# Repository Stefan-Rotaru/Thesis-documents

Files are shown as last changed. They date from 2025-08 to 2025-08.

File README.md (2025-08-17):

#Thesis code
Roll stabilization lab
==================================

Prerequisites
-------------
• Python 3.12+  
• Arduino IDE  
• Servo.h Arduino Library (https://www.arduino.cc/reference/en/libraries/servo/)

Usage
-----
1. Upload the controller to the Arduino:
   - Plug-in the Arduino board  
   - Open the "PID_Arduino" file,  then the "PID_Arduino.ino" script  
   - Select your board and port  
   - Click Upload

2. Record data to a text file:  
   - python script.py

3. Plot the data :
  - python plots.py --trim= a test_b.txt
  - Replace a by the trim needed
  - Replace b by the test to plot

Configuration
-------------
 - In "PID_Arduino.ino" (line 175) tweak "Kp", "Ki", "Kd" to tune your controller.
 - On line 160 of "PID_Arduino.ino" you can change the “setpoint” for your target roll angle.
 - In "script.py" make sure the serial "port = 'COM3'" matches your board.

Encoder error
-------------
Spikes might occur due to encoder's measurement error

#Solidworks Assembly 3D
=======================
Contains the solidworks files. Assem1 is the whole assembly of the device

#Thesis video
=============
Contains the videos of the experimental tests. They are also available in the issues tab.

#Technical drawings
===================
Contrains the technical drawings of the aluminium machined version of the device

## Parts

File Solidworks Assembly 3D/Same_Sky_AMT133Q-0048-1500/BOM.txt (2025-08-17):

3DX_Same_Sky_Supplier: Same Sky
3DX_Same_Sky_Description: AMT13 Axial, Quadrature Line Driver, 48 PPR, 15 mm Bore
3DX_Same_Sky_Part Number: AMT133Q-0048-1500

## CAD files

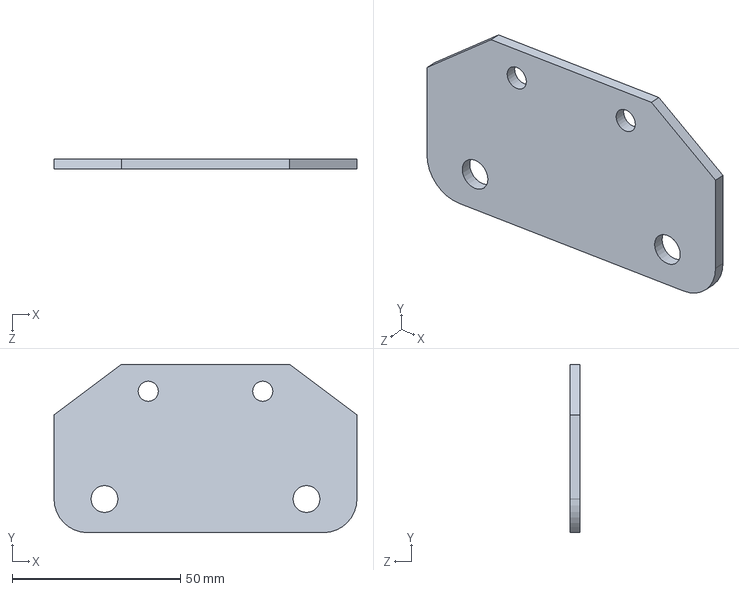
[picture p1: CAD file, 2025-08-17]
Solidworks Assembly 3D/Attachement a la base.SLDPRT
90.0 x 50.0 x 3.00 mm

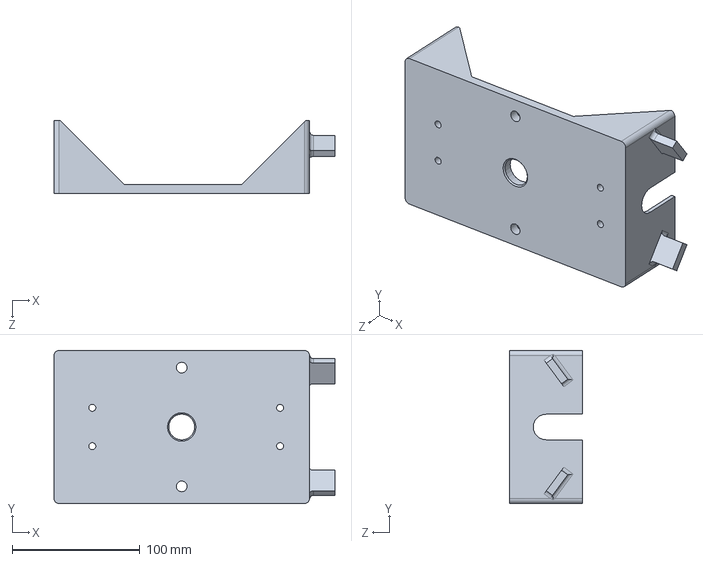
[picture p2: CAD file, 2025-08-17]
Solidworks Assembly 3D/chassis.SLDPRT
220.0 x 120.0 x 57.0 mm

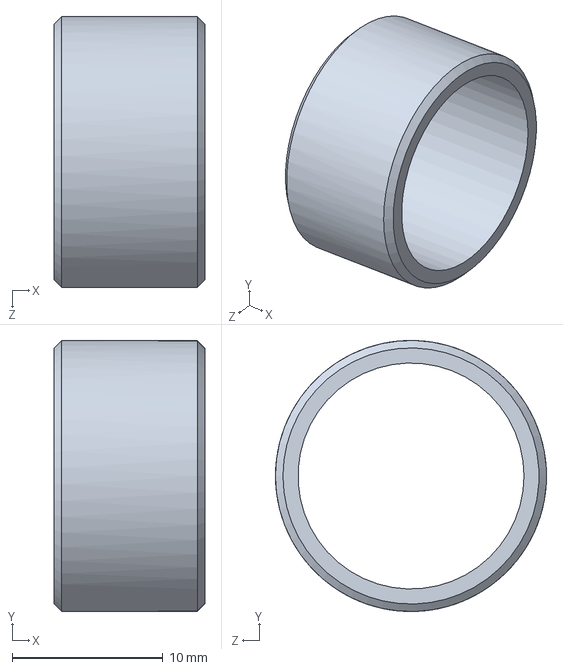
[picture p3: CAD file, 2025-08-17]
Solidworks Assembly 3D/Part1.SLDPRT
10.0 x 18.0 x 18.0 mm

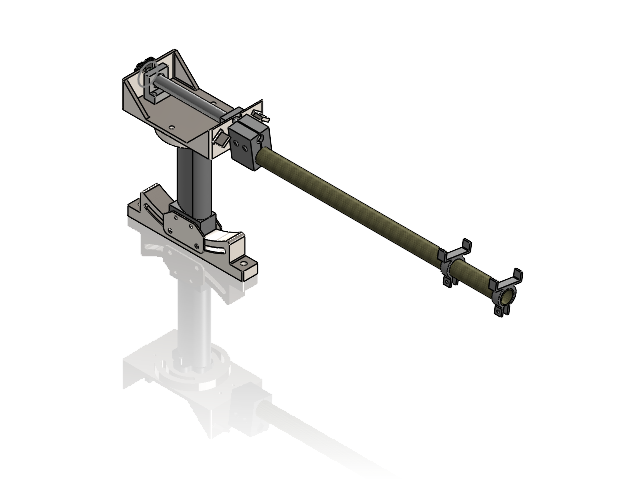
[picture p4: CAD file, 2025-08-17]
Solidworks Assembly 3D/Assem1.SLDASM
Base arc de cercle
Support
Attachement a la base x 2
Support dervie
Spacer
RCB6-30 x 2
PSFAJEU20-164-F40-P15-T60
chassis
BGLKS6902ZZ-30_b x 2
bearing_6902 x 2
RRING28 x 2
shaft_holders x 2
shaft_carbon
Same_Sky_SPACER_AMT13
Same_Sky_PIN_AMT13 x 6
Same_Sky_PIN_2_5MM-4_7MM x 2
Same_Sky_RECEIVER_PCB_AMT13
Same_Sky_ROTOR_AMT13
Same_Sky_SET_SCREW_2_5D-3L-0_45P
Same_Sky_HUB_15MM
Same_Sky_TRANSMITER_PCB_AMT13
Same_Sky_BM18B-ZPDSS-TF
Same_Sky_INJECTION_MOLDING_CHASSIS
Same_Sky_INJECTION_MOLDING_COVER
Berceau x 2

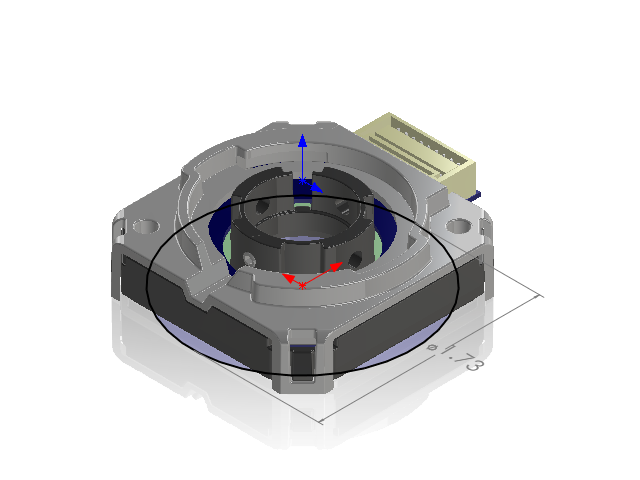
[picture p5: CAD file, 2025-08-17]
Solidworks Assembly 3D/Same_Sky_AMT133Q-0048-1500/Same_Sky_CUI_DEVICES_AMT133S-0048-1500.SLDASM
Same_Sky_SPACER_AMT13
Same_Sky_PIN_AMT13 x 6
Same_Sky_PIN_2_5MM-4_7MM x 2
Same_Sky_RECEIVER_PCB_AMT13
Same_Sky_ROTOR_AMT13
Same_Sky_SET_SCREW_2_5D-3L-0_45P
Same_Sky_HUB_15MM
Same_Sky_TRANSMITER_PCB_AMT13
Same_Sky_BM18B-ZPDSS-TF
Same_Sky_INJECTION_MOLDING_CHASSIS
Same_Sky_INJECTION_MOLDING_COVER

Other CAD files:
Solidworks Assembly 3D/Same_Sky_AMT133Q-0048-1500/Same_Sky_TRANSMITER_PCB_AMT13(Axial).SLDASM
Solidworks Assembly 3D/Bumper/ULBYS20-30-M8.sldasm
Solidworks Assembly 3D/SOLIDWORKS/BGLKS6902ZZ-30.sldasm
Solidworks Assembly 3D/Same_Sky_AMT133Q-0048-1500/Same_Sky_ROTOR_AMT13(1500).SLDASM
Solidworks Assembly 3D/Same_Sky_AMT133Q-0048-1500/Same_Sky_RECEIVER_PCB_ASM.SLDASM
Solidworks Assembly 3D/Same_Sky_AMT133Q-0048-1500/Same_Sky_SPACER_AMT13_ASM.SLDASM
Solidworks Assembly 3D/Same_Sky_AMT133Q-0048-1500/Same_Sky_PCB_AMT13(Axial, 1500).SLDASM
Solidworks Assembly 3D/Bumper/ULBYS20-30-M8_b.sldprt
Solidworks Assembly 3D/Same_Sky_AMT133Q-0048-1500/Same_Sky_INJECTION_MOLDING_CHASSIS.SLDPRT
Solidworks Assembly 3D/SOLIDWORKS/RRING28.sldprt
Solidworks Assembly 3D/Bumper/SCB8-12_1.sldprt
Solidworks Assembly 3D/SOLIDWORKS/BGLKS6902ZZ-30_b.sldprt
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

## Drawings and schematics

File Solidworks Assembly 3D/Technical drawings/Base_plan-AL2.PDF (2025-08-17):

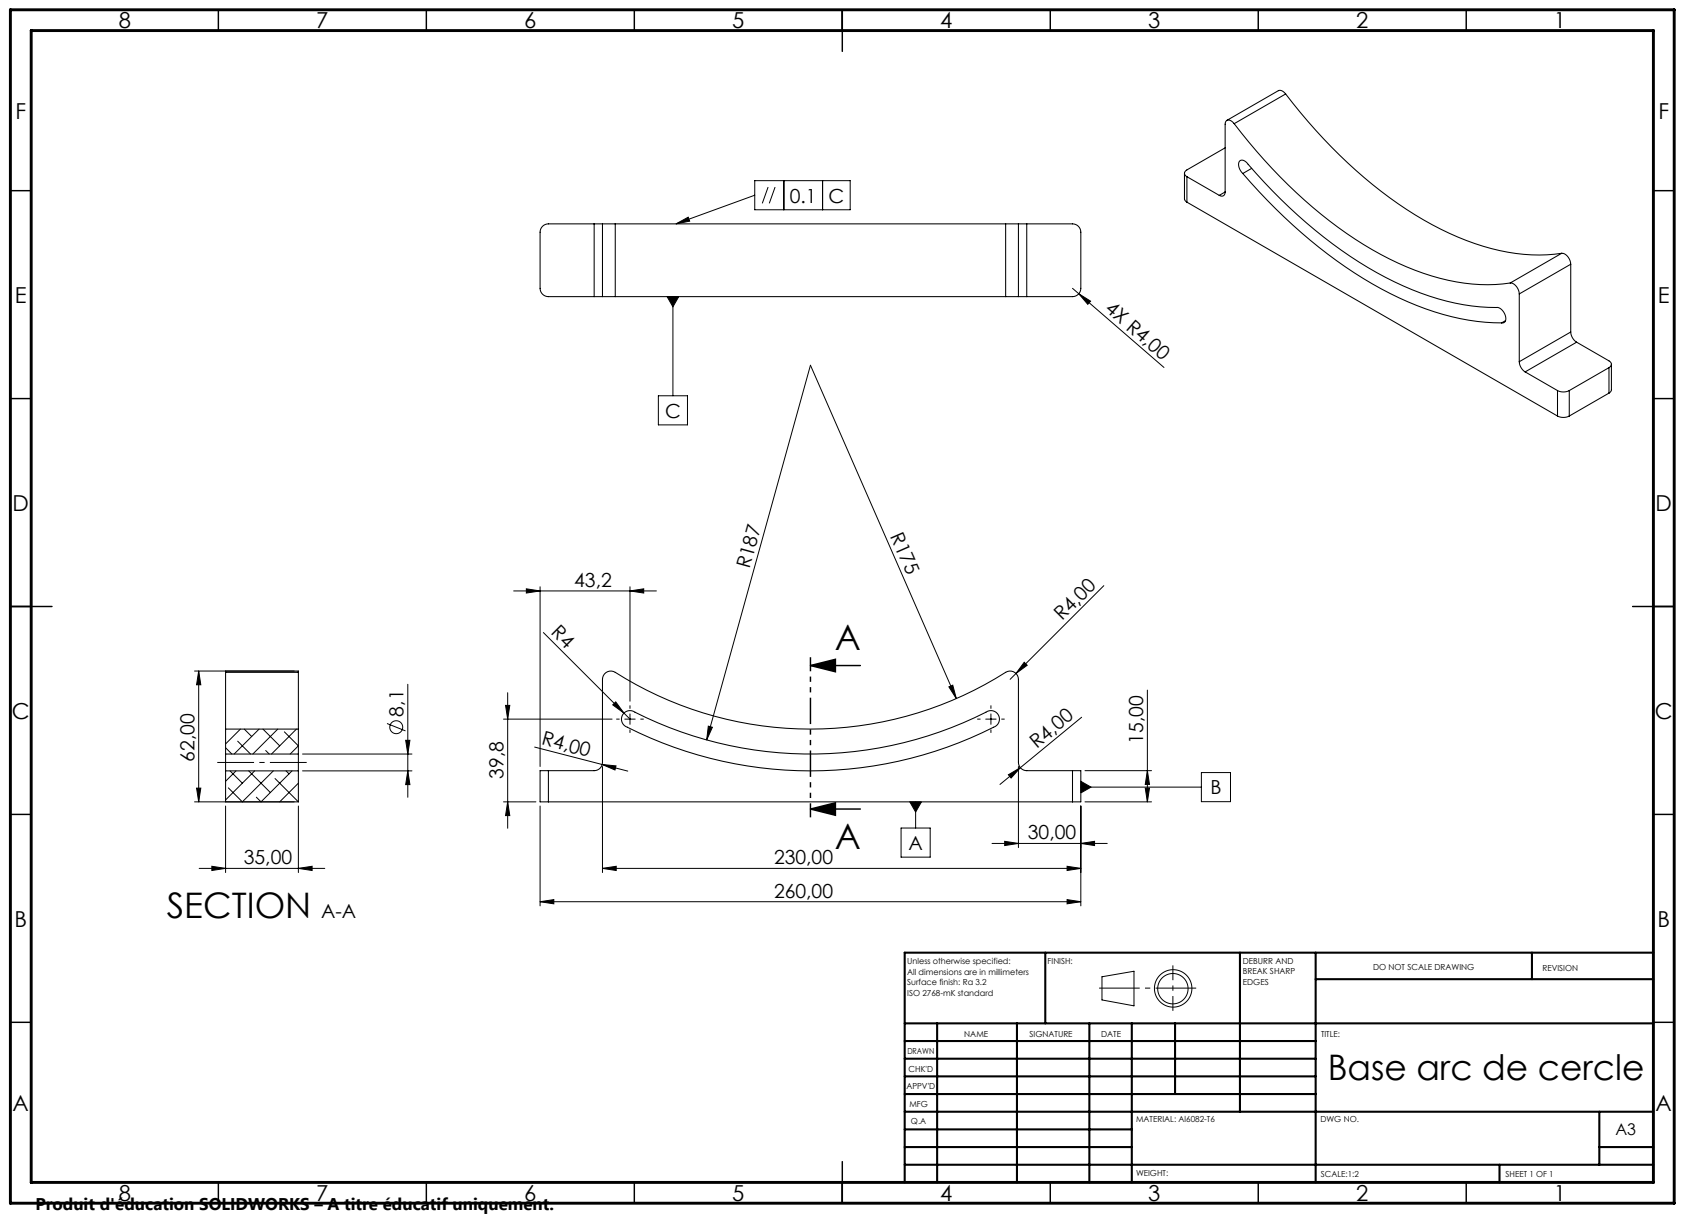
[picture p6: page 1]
SECTION A-A; FINISH:; DEBURR AND; BREAK SHARP; DO NOT SCALE DRAWING; REVISION; SCALE:1:2; SHEET 1 OF 1

Unless otherwise specified:
All dimensions are in millimeters
Surface finish: Ra 3.2
ISO 2768-mK standard

NAME | SIGNATURE | DATE | | | | TITLE: Base arc de cercle

DRAWN
CHK'D
APPV'D
MFG
Q.A | | | | MATERIAL: Al6082-T6 | DWG NO. | A3

Produit d'éducation SOLIDWORKS – A titre éducatif uniquement.

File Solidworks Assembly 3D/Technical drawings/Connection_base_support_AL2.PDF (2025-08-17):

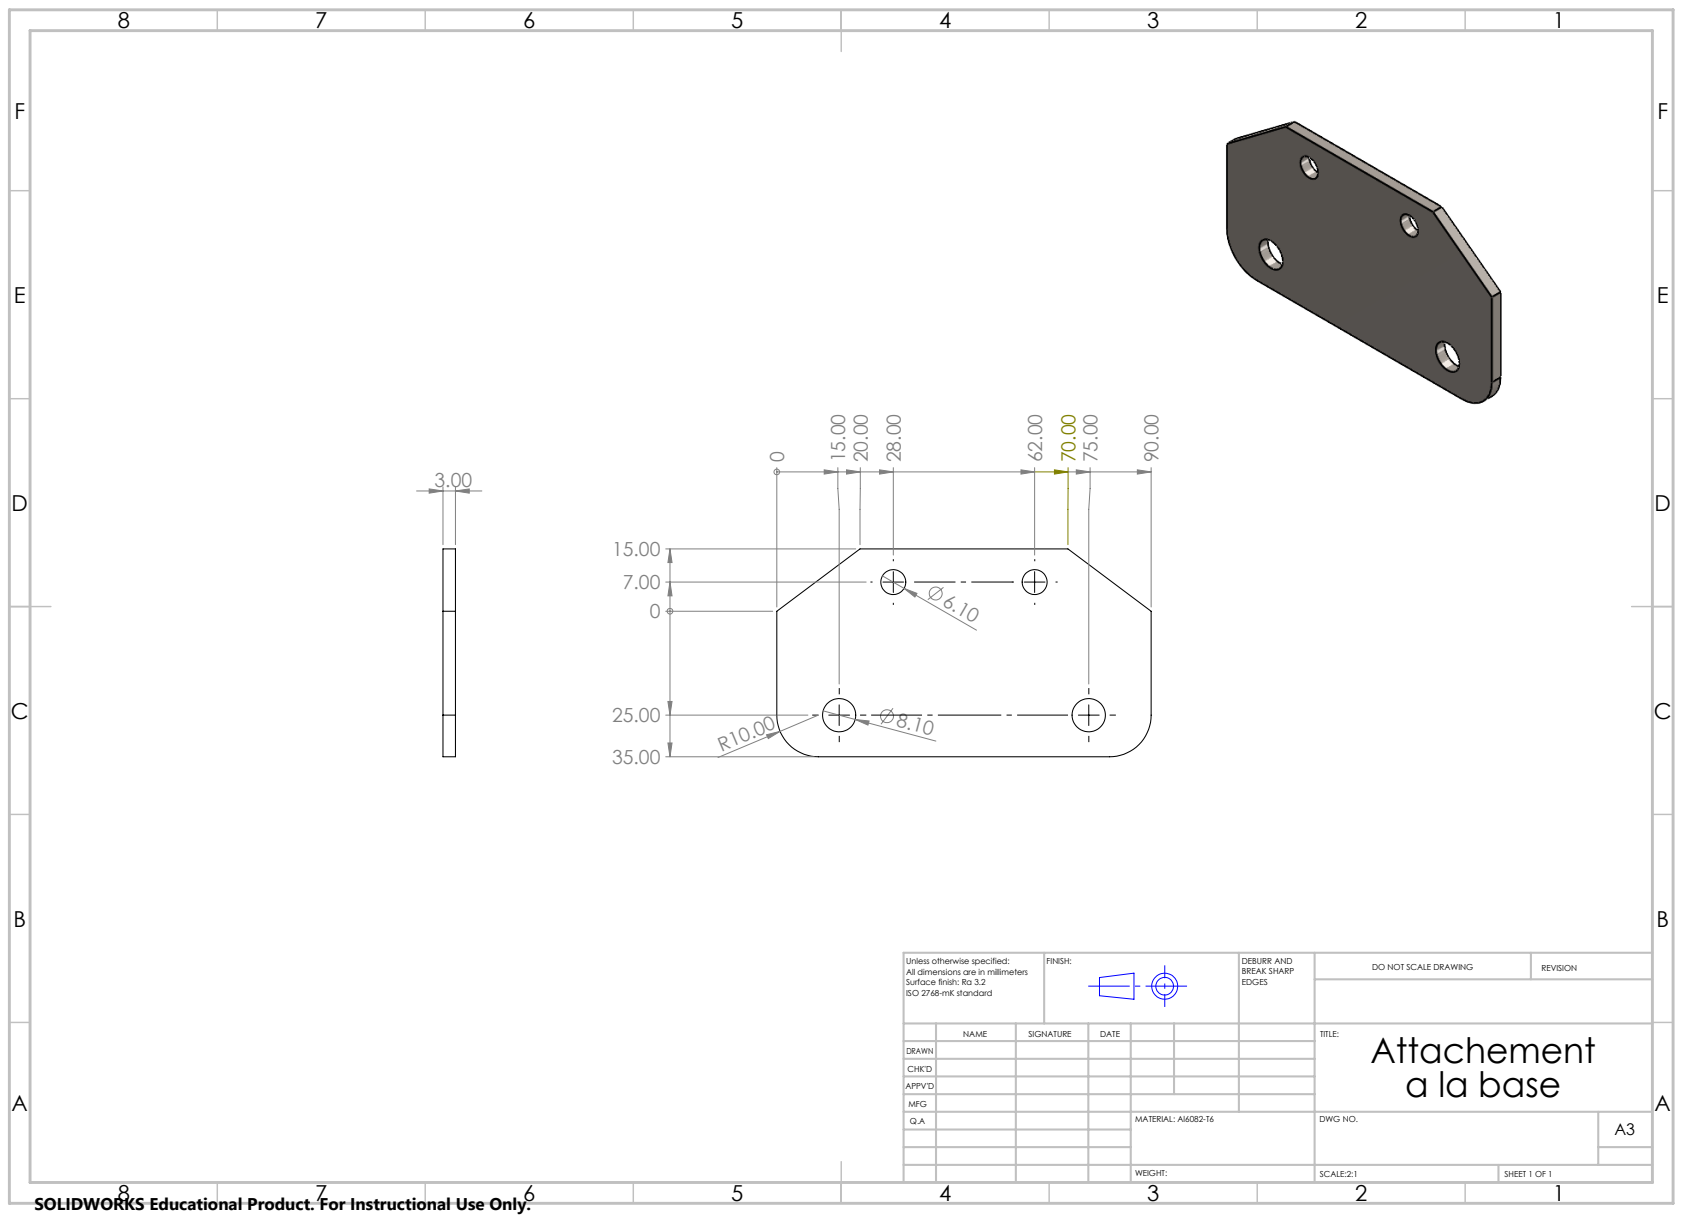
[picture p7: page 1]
FINISH:; DEBURR AND; BREAK SHARP; DO NOT SCALE DRAWING; REVISION; SCALE:2:1; SHEET 1 OF 1

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

NAME | SIGNATURE | DATE | | | | TITLE: Attachement a la base

DRAWN
CHK'D
APPV'D
MFG
Q.A | | | | MATERIAL: Al6082-T6 | DWG NO. | A3

SOLIDWORKS Educational Product. For Instructional Use Only.

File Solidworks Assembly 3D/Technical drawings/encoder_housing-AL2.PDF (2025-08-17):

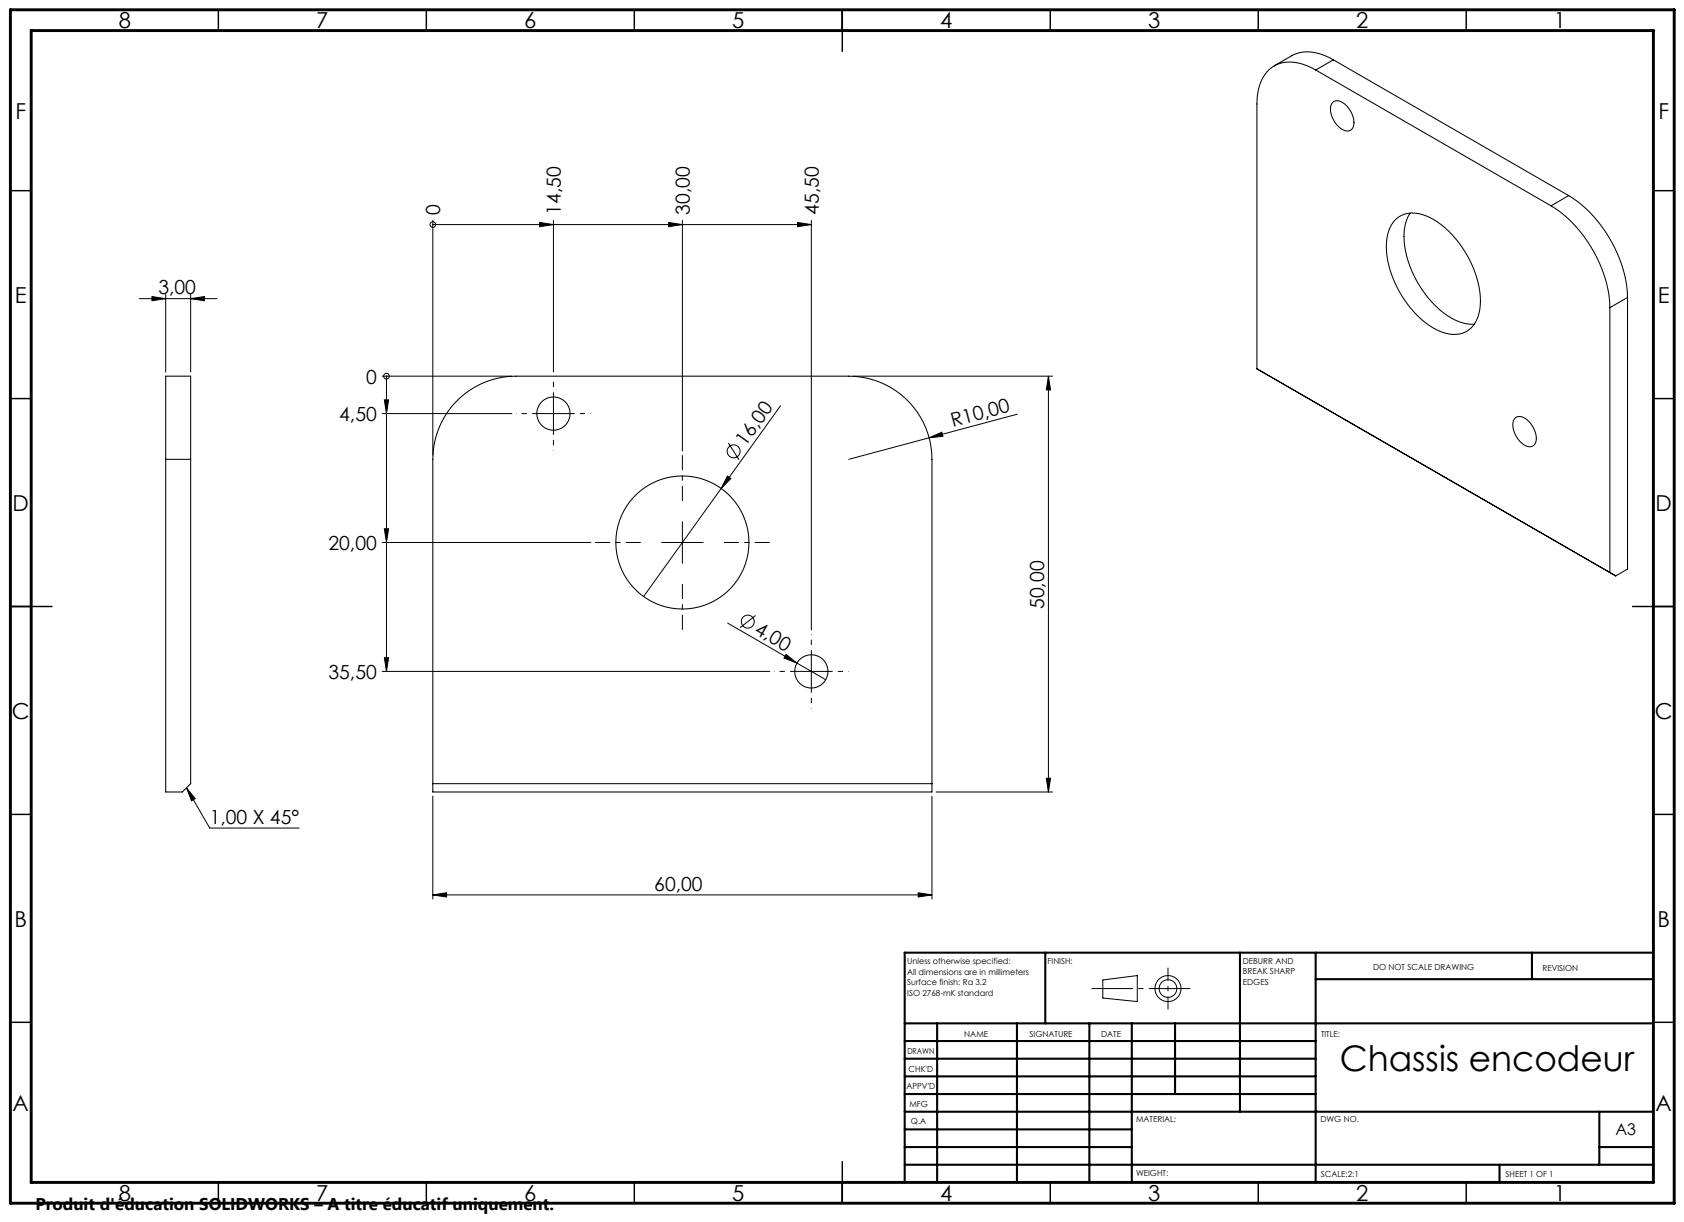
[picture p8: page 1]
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

NAME | SIGNATURE | DATE | | | | TITLE: Chassis encodeur

DRAWN
CHK'D
APPV'D
MFG
Q.A | | | | MATERIAL: | DWG NO. | A3

Produit d'éducation SOLIDWORKS – A titre éducatif uniquement.

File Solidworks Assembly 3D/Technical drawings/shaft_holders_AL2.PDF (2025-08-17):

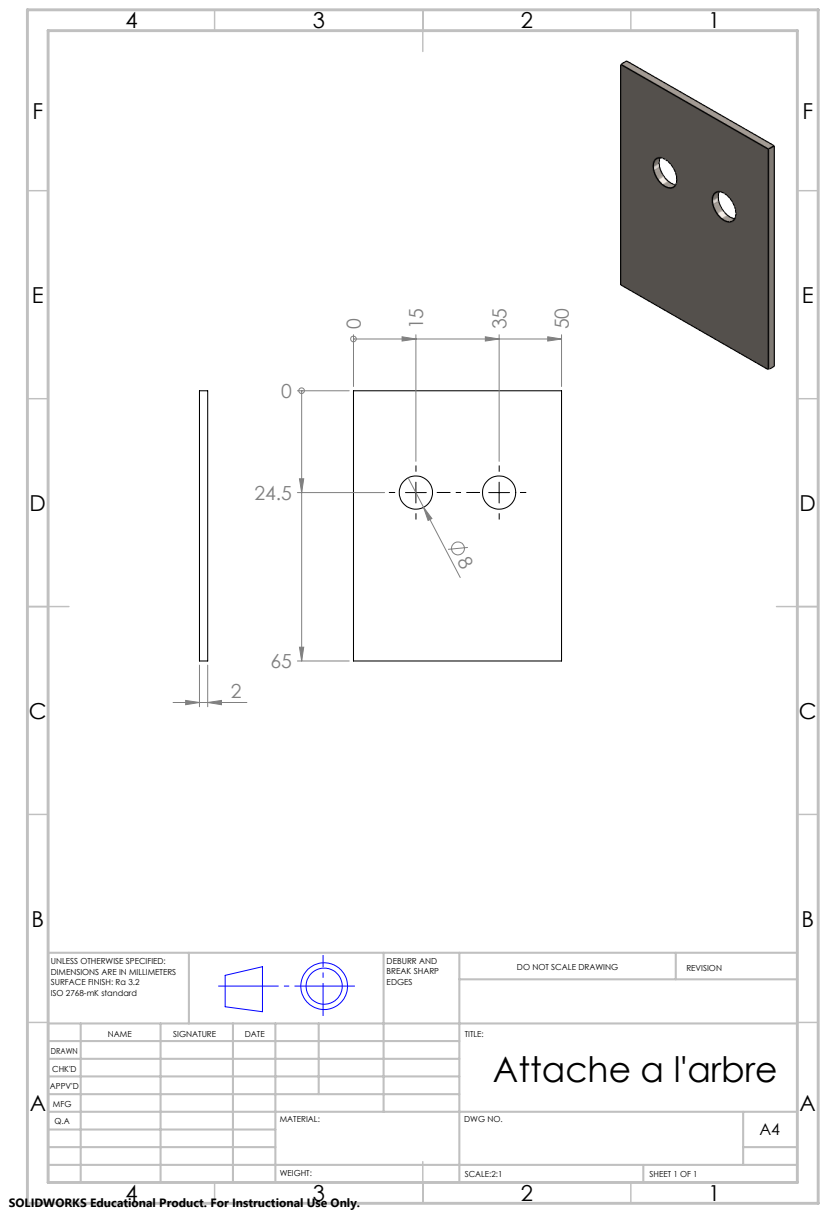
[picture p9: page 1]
DEBURR AND BREAK SHARP; DO NOT SCALE DRAWING; REVISION; SCALE:2:1; SHEET 1 OF 1

UNLESS OTHERWISE SPECIFIED:
DIMENSIONS ARE IN MILLIMETERS
SURFACE FINISH: Ra 3.2
ISO 2768-mK standard

NAME | SIGNATURE | DATE | | | | TITLE: Attache a l'arbre

DRAWN
CHK'D
APPV'D
MFG
Q.A | | | | MATERIAL: | DWG NO. | A4

SOLIDWORKS Educational Product. For Instructional Use Only.

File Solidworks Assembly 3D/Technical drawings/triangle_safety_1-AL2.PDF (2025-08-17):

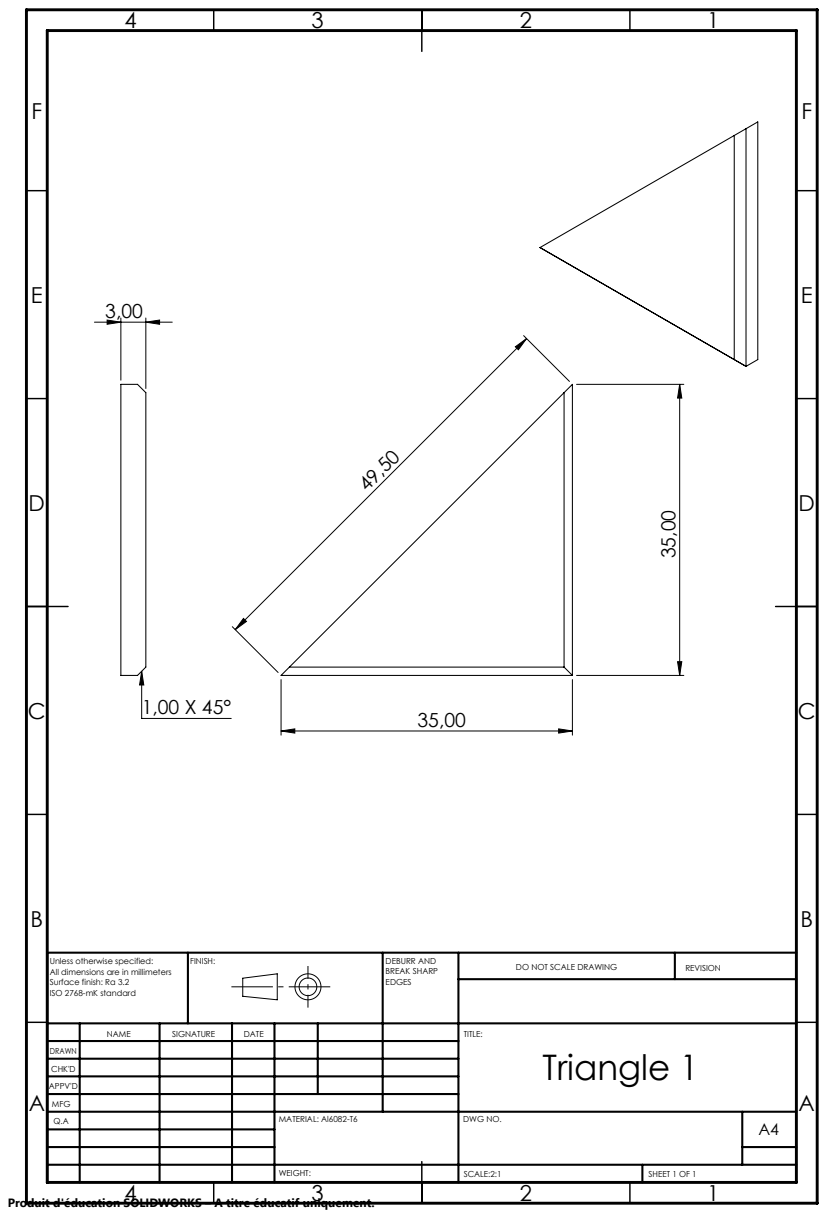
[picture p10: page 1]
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

NAME | SIGNATURE | DATE | | | | TITLE: Triangle 1

DRAWN
CHK'D
APPV'D
MFG
Q.A | | | | MATERIAL: Al6082-T6 | DWG NO. | A4

Produit d'éducation SOLIDWORKS – A titre éducatif uniquement.

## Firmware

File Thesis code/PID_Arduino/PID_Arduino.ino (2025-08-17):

// ----- Do not modify -----
#define USB_BAUDRATE         115200
#define RS485_BAUDRATE       2000000
#define RESOLUTION            12
#define RS485_ENC0            0x54
#define RS485_ENC1            0x58
#define RS485_POS             0x00
#define RS485_TURNS           0x01
#define RS485_ZERO            0x02
#define RS485_RESET           0x03
#define RS485_T_RE            8
#define RS485_T_DE            8
#define RS485_T_DI            18
#define RS485_T_RO            19
#define RS485_T_TX            0
#define RS485_T_RX            1 
#define ZERO_BUTTON           13
// -------------------------

#include <Servo.h>
#include <math.h>
// Pin d'attache sur l'arduino des servos-moteurs
#define SERVO_L_PIN 11
#define SERVO_R_PIN 10
Servo servoL, servoR;
float phi_prev;

// Structure reprenant toute les valeurs nécessaires pour le PID
struct control_values {
  float control;
  float prev_error;
  float integral;
};

// Fonction de return de la structure
control_values create_struct(){
  control_values result;
  result.control = 0;
  result.prev_error = 0;
  result.integral = 0;
  return result;
}

control_values control_val = create_struct();

// Fonction PID
void PID_controller(float setpoint, float measured, float Kp, float Ki, float Kd, float dt)
{
  float error = setpoint - measured;

  float P = Kp * error;
  float D = Kd * (error - control_val.prev_error) / dt;
  control_val.integral += Ki * error * dt;
  float U = P + control_val.integral + D;

  // Anti-windup
  if (U >= 20 * M_PI/180){ 
    control_val.integral -= Ki * error * dt;
    U = 20 * M_PI/180;
  }
  else if (U <= -20 * M_PI/180){
    control_val.integral -= Ki * error * dt;
    U = -20 * M_PI/180;
  }
  control_val.control = U;
  control_val.prev_error = error;
}

// Delais entre chaque boucle : dt
float time = 0;
float dt = 0.02;

void setup()
{ 
  // ----- Ne pas modifier -----
  setup_AMT();
  // ---------------------------

  // Setup en remetteant les ailerons droits et en attandant 2 secondes pour que l'avion se restabilise.
  float phi_prev = 0;
  servoL.attach(SERVO_L_PIN);
  servoL.write(101);
  servoR.attach(SERVO_R_PIN);
  servoR.write(94);
  delay(2000);
}

void loop()
{
  // ----- Ne pas modifier -----
  float angle_of_roll = 0;
  uint8_t addresses[1] = {RS485_ENC0};
  if(digitalRead(ZERO_BUTTON) == LOW)
  {
    for(int encoder = 0; encoder < sizeof(addresses); ++encoder)
    {
      Serial.println("Zeroing...");
      sendCommandRS485(addresses[encoder] | RS485_ZERO);
      delay(100); 
      Serial.println("Zero done. Resetting...");
      sendCommandRS485(addresses[encoder] | RS485_RESET);
      delay(500); 
    }
    while(digitalRead(ZERO_BUTTON) == LOW)
    {
      delay(100);
    }
  }
  for(int encoder = 0; encoder < sizeof(addresses); ++encoder)
  {
    while (Serial1.available()) Serial1.read();
    sendCommandRS485(addresses[encoder] | RS485_POS);
    delayMicroseconds(400);
    int bytes_received = Serial1.available();
    if (bytes_received == 2)
    {
      uint16_t currentPosition = Serial1.read(); 
      currentPosition |= Serial1.read() << 8;   
      if (verifyChecksumRS485(currentPosition))
      {
        currentPosition &= 0x3FFF;
        if (RESOLUTION == 12)
        {
          currentPosition = currentPosition >> 2;
        }

        // Lecture de l'angle et transformation en radians
        const uint16_t HALF_TURN      = 4096 / 2;
        int16_t signedCounts = currentPosition;      
        if (signedCounts >= HALF_TURN)              
          signedCounts -= 4096;          
        angle_of_roll = -(360.0f * signedCounts) / 4096;
      }
      else
      {
        Serial.print("Encoder #");
        Serial.print(encoder, DEC);
        Serial.println(" error: Invalid checksum.");
      }
    }
    else
    {
      Serial.print("Encoder #");
      Serial.print(encoder, DEC);
      Serial.print(" error: Expected to receive 2 bytes. Actually received ");
      Serial.print(bytes_received, DEC);
      Serial.println(" bytes.");
    }
    while (Serial1.available()) Serial1.read();
  }
  // --------------------

  // ------ Partie modifiable ------
  float setpoint = 0; // Setpoint en radians

  // Ici on peut mettre differentes position de roulis en fonction du temps. Depend du test qu'on veut réaliser.
  // if (time < 20){
  //   setpoint = 0;
  // }
  if (time >= 13){
    setpoint = 10* M_PI/180;
  }
  // if (time >= 16){
  //   setpoint = 0* M_PI/180;
  // }
  // if (time >= 19){
  //   setpoint = 20* M_PI/180;
  // }
  // if (time >= 22){
  //   setpoint = 0* M_PI/180;
  // }

  // ----- PID -----
  // Coefficients  PID
  float Kp = 1.1;
  float Ki = 1.2;
  float Kd = 0.7;
  PID_controller(setpoint, angle_of_roll * M_PI / 180, Kp, Ki, Kd, dt);

  // Transformer l'angle de control en un angle de servomoteur
  float delta_s_R = control_val.control * 180/M_PI * 1200/95 + 1470;
  float delta_s_L = control_val.control * 180/M_PI * 1200/95 + 1580; 

  // Commande au servo-moteur
  servoL.writeMicroseconds(delta_s_L);
  servoR.writeMicroseconds(delta_s_R);

  // Récuperation des données
  Serial.print(angle_of_roll);
  Serial.print(" ,");
  Serial.print(control_val.control * 180/M_PI);
  double p_dot = ((angle_of_roll - phi_prev)) / dt;
  Serial.print(" ,");
  Serial.println(p_dot);
  phi_prev = angle_of_roll;

  // Boucle temporelle
  time += dt;
  delay(dt * 1000);
}


// ---- Ne pas modifier -----
void setup_AMT()
{
  pinMode(RS485_T_RE, OUTPUT);
  pinMode(RS485_T_DE, OUTPUT);
  pinMode(RS485_T_RO, INPUT_PULLUP);
  pinMode(ZERO_BUTTON, INPUT_PULLUP); 
  Serial.begin(USB_BAUDRATE);
  Serial1.begin(RS485_BAUDRATE);
}

bool verifyChecksumRS485(uint16_t message)
{
  uint16_t checksum = 0x3;
  for(int i = 0; i < 14; i += 2)
  {
    checksum ^= (message >> i) & 0x3;
  }
  return checksum == (message >> 14);
}

void sendCommandRS485(uint8_t command)
{
  PORTH |= 0b01100000; 
  delayMicroseconds(10); 
  Serial1.write(command); 
  while (!(UCSR1A & _BV(TXC1))); 
  PORTH &= 0b10011111; 
}
